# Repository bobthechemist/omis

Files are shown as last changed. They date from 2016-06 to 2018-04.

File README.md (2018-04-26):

## Open Millifluidic Inquiry System ##

The Thingiverse version

The **Open Millifluidic Inquiry System** (OMIS) is a platform for lab-on-a-chip technologies and miniaturized analysis systems. It is a 3D printed, Arduino-based science and engineering project that allows the end-user (student/teacher/hobbyist) to explore the science of fluids. OMIS currently has two parts. The first is a syringe pump constructed from 3D printed parts, an inexpensive stepper motor and some items from the local hardware store. The second part is a “millifluidic device” which is also 3D printed. OMIS is designed with learning and inquiry in mind, and all elements of the design have been created to encourage exploration.

## Quick start
1. Print the parts located in the STL directory.
2. Purchase the items in the [Bill of Materials](documentation/BOM.md).
3. Follow the [build guide](documentation/BuildGuide.md).
4. Design your circuit using [this Adafruit guide](https://learn.adafruit.com/adafruit-arduino-lesson-16-stepper-motors/parts?view=all).
5. Upload the sketch in the software directory to your Arduino.

## Resources
- [The github](http://www.github.com/bobthechemist/omis) repository will be used for version management and issue tracking.  This will be true for design files, software and lessons/activities.
- My [personal webpage](http://www.bobthechemist.com/omis) will be the source for commentary and any opinions I have on the project.
- The build at [Thingiverse](http://www.thingiverse.com/thing:1646999) will remain as the original version for historical reasons.

----------

  
This work is licensed under a <a rel="license" href="http://creativecommons.org/licenses/by-nc-sa/4.0/">Creative Commons Attribution-NonCommercial-ShareAlike 4.0 International License</a>.

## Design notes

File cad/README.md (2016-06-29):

##CAD files

###Syringe pump files
The syringe pump consists of three design files (one for each of the components of the syringe pump), a global variables and functions file and a summary file.  The CAD files have been designed such that the typical changes an end user may make (support rod and lead screw dimensions, fastener types, syringe properties) can all be customized within a single file.

- **sp_global** is the location for all global variables and functions used by the other design files.
- **syringepump** allows the end user to view the entire project.  It is not meant for actual use but to ensure that features and spacing is consistent throughout the design.
- **sp\_motor\_assembly** contains the gear train and components used to hold the stepper motor in place.
- **sp_carriage** is the moving piece that pushes the syringes
- **sp_idler** is the end cap that supports the structural and threaded rods, and also provides support for the syringes.

There are currently two example millifluidic devices, one with side ports and one with top-face ports.  The side-port version uses cylindrical channels and the top-face port version uses rectangular channels.  These devices are designed with exploration in mind, while we identify best practices for 3D printed millifluidic device fabrication.

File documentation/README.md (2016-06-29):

#Table of contents

- have a look at the [Bill of materials](BOM.md) to see what you need to buy.
- Once you have, look at the [Build Guide](BuildGuide.md) for instructions on how to construct the syring pump.

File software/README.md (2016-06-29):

# Arduino sketch and schematic

## Electronics

The breadboard layout, shown below, is identical to the one described in the [Adafruit tutorial on stepper motors](https://learn.adafruit.com/adafruit-arduino-lesson-16-stepper-motors/parts?view=all).  That tutorial is a prerequisite to building the electronics/software side of OMIS.  

breadboard layout

## Sketch

The sketch is broken up into several components, in hopes to make it easier to modify the code.  Note that OMIS uses a modified version of the [Arduino stepper library](https://www.arduino.cc/en/Reference/Stepper).  The primary reason for the modified version is to allow for non-integer RPM values to be passed to the motor.  It also has some helpful(?) functions related to the pump such as determining the volume flow rate for a given motor speed.   Additionally, it contains the operations to be performed when receiving commands via the Serial line.

The other component to the sketch is the Command Parser, which is a very primitive class that deals with serial communication and performs some basic sanity checking.

To install, simply move the software directory and its contents into your Arduino directory, and rename the directory syringepump.

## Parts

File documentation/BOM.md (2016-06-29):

##OMIS Bill of Materials
*Please note this BOM is for the pre-release version (< 1.0) of OMIS and is subject to change*

### General tools and equipment
- 3D printer

    All components of this project were printed on a home-built [Makerfarm](www.makerfarm.com) Prusa 8" i3v.  Presumably, a commercial printer will provide comparable (or more likely, superior) print quality.
- Filament
    
    Builds were tested with PLA (eSun) and PETG (Gizmodorks).  The latter is preferred due to its increased chemical resistance relative to PLA and the structural performance (it is less brittle).

- M3 hex key and wrench
- Exacto knife
- Sandpaper
- Adjustable wrench
- Needle nosed pliers
- Helping hand with magnifier or dissecting microscope 

### syringe pump
- 1/4" steel rod, 140 mm length, (2)
- 1/4"-20 TPI threaded steel rod, 155 mm length (1)
- 5V DC small reduction stepper motor from [Adafruit](https://www.adafruit.com/products/858).
- M3x10 hex-bolts (4)
- M3x16 hex bolts (2)
- M3x25 hex bolts (3)
- M3 hex nuts (12)
- 1/4" 20 TPI nuts (3)
- 1/4" 20 TPI jamnuts (2)
- Syringes

    The default configuration uses a 3-mL HSW luer slip eccentric syringe which can be found at [Restek](http://www.restek.com/catalog/view/8027) although I purchased my batch from Fisher Scientific (and they apprently no longer sell them).  A different syringe can be used by adjusting the parameters in the global file.

### fluidics system
- flexible tubing with an outer diameter of approximately 1.8 mm
- quick-setting epoxy

### controller
- Arduino Uno or similar
- L293D dual H bridge or similar
- hookup wire

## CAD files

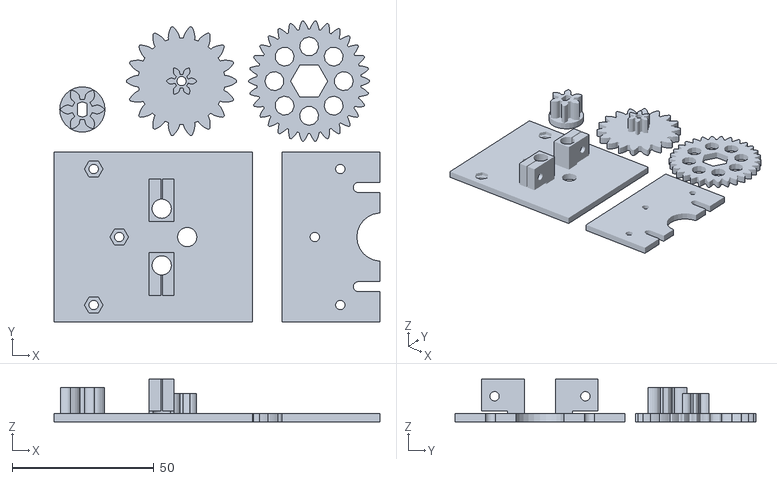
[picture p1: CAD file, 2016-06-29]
stl/motor_assembly.stl
115.0 x 106.2 x 15.0

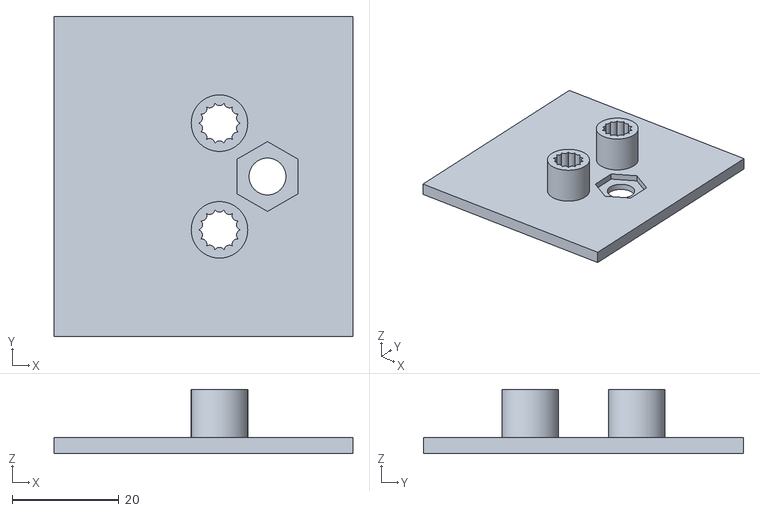
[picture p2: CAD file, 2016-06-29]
stl/carriage.stl
56.0 x 60.0 x 12.0

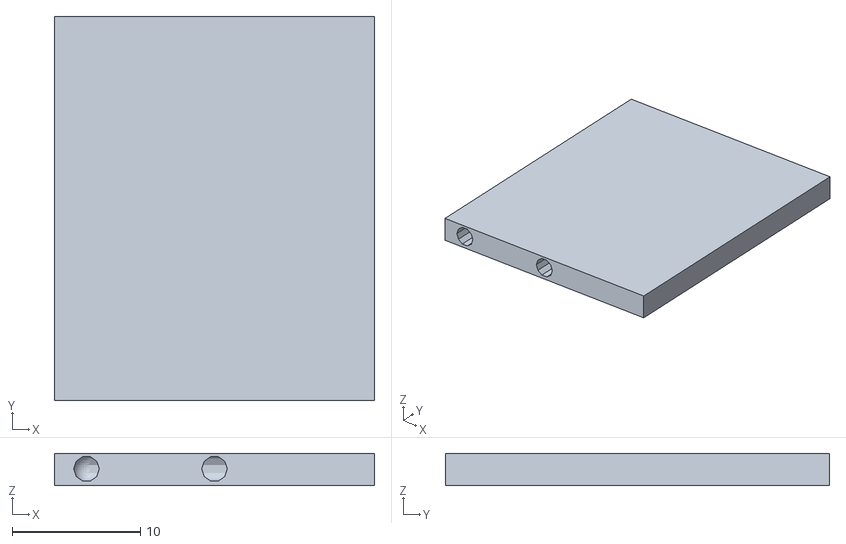
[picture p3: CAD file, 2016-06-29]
stl/cylindricalChannels.stl
25.0 x 30.0 x 2.50

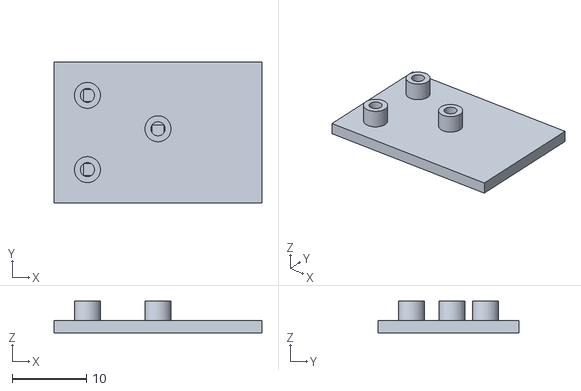
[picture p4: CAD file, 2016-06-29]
stl/rectangularChannels.stl
28.0 x 19.0 x 4.30

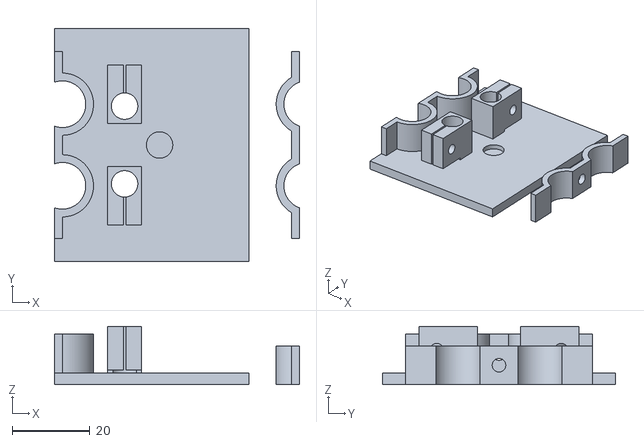
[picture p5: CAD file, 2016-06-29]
stl/idler.stl
63.0 x 60.0 x 15.0

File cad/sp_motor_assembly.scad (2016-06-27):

// Autotitrator motor assembly
/* 
This version incorporates a compound gear train to improve the
torque applied to the lead screw.  Some adjustments made to the
orientation of the suppor rod clamps to allow for printing on one 
side only.

Unlike the first version, this one incorporates gears into the
assembly as opposed to having a separate file.
*/

include <sp_global.scad>;
use <MCAD/involute_gears.scad>;

print_mode = false;

// Gear pitch radii
// 0 is motor, 1 is larger cmpd, 2 is smaller cmpd and 3 is driven
pitchRadius = [5.8333, 17.5, 4, 20];
// Where to put the three support screws, one is aligned with the 
//   compound gear.
gearboxSupport = [ [0,0.4*baseDim[y],0.8*baseDim[z]],
                [0,-0.4*baseDim[y],0.8*baseDim[z]],
                [0,0,
                trodPosition[z]+pitchRadius[2]+pitchRadius[3]]];

// Build up modules
module base(){
    difference(){
        union(){
            translate([0,0,1/2*baseDim[z]])
            cube(baseDim,center=true);
            structuralRodSupports();
        }
        union() {
            threadedRodCutout();
            structuralRodCutout();
            gearboxSupports();
        }
    }
}

module gearboxSupports(){
    // gearbox support holes
    for (i = gearboxSupport) {
        translate(i)
        rotate(90,[0,1,0]){
            cylinder(d=fast[nutDiameter],
                h=1.2*baseDim[y],center=false,$fn=6);
            cylinder(d=fast[boltDiameter],
                h=1.2*baseDim[y],center=true,$fn=25);
        }
    }   
}

module structuralRodSupports() {
    for(i = [ [-1, false], [1, true] ] ){
        translate([baseDim[x]/2, i[0]*rodPosition[y], rodPosition[z]])
        rodClamp(rot=i[1]);
    }    
}

module gearBox(){
    shaft_z = trodPosition[z]+pitchRadius[0] + pitchRadius[1] +
        pitchRadius[2] + pitchRadius[3];
    cmpd_z = trodPosition[z] + pitchRadius[2] + pitchRadius[3];
    difference() {
        union() {
            translate([0,0,1/2*baseDim[z]])
            cube(baseDim,center=true);
            translate([0,0,cmpd_z])
            *rotate(90,[0,1,0]){
                cylinder(d=2.7,h=15,$fn=10);
                cylinder(d=5,h=5);
            }
        }
        union() {
            // motor cutout
            translate([-baseDim[x]/1.9,-baseDim[y]/1.9,baseDim[z]])
            cube([baseDim[x]*1.1,baseDim[y]*1.1,200]);
            translate([0,0,shaft_z])
            rotate(90,[0,1,0])
            cylinder(d=17,h=1.1*baseDim[x],center=true,$fn=25);
            // motor support cutout
            for (i = [-1,1] ) {
                translate([0,i*35/2,shaft_z-8])
                rotate(90,[0,1,0])
                cylinder(d=3.5,h=2.2*baseDim[x],center=true,$fn=25);
                translate([-baseDim[x]/1.9,i*35/2-3.5/2,shaft_z-8])
                cube([baseDim[x]*1.1,3.5,25]);
            }
            // gearbox screw holes
            translate([0,0,cmpd_z])
            rotate(90,[0,1,0])
            cylinder(d=fast[boltDiameter],
                h=1.2*baseDim[y],center=true,$fn=25);
            // gearbox support holes
            for (i = gearboxSupport) {
                translate(i)
                rotate(90,[0,1,0])
                cylinder(d=fast[boltDiameter],
                    h=1.2*baseDim[y],center=true,$fn=25);
            }
            // trim unused part of plate
            translate([0,0,0]);
            cube(1.01*baseDim,center=true);
                
        }
    }
}

module gearDriven(){
    gear_z = 3;
    difference(){
        gear(circular_pitch = 240,
            number_of_teeth = 30, 
            rim_thickness = gear_z,
            hub_thickness = 0,
            gear_thickness = gear_z,
            bore_diameter = 0,
            circles = 8,
            rim_width = 1.5,
            hub_diameter = 15
            );
        cylinder(d=trod[nutDiameter],h=2.1*gear_z,center=true,$fn=6);
    }
}

module gearCompound(){
    gear_z1 = 3;
    gear_z2 = 7;
    difference(){
        union(){
            gear (circular_pitch = 350,
                number_of_teeth = 18,
                rim_thickness = gear_z1,
                hub_thickness = 0,
                gear_thickness = gear_z1,
                bore_diameter = 0
            );
            translate([0,0,gear_z1])
            gear (circular_pitch = 240,
                number_of_teeth = 6,
                rim_thickness = gear_z2,
                hub_thickness = 0,
                gear_thickness = gear_z2,
                bore_diameter = 0,
                rim_width = 0,
                hub_diameter=0
            );
        }
        cylinder(d=fast[boltDiameter]+0.05,
            h=2.1*(gear_z1+gear_z2),center=true,$fn=10);
    }
}

module gearMotor() {
    gear_z = 9;
    difference() {
        translate([0,0,15])
        rotate(180,[0,1,0])
        gear (circular_pitch = 350,
            number_of_teeth=6,
            rim_thickness = gear_z,
            hub_thickness = 12,
            gear_thickness = gear_z,
            bore_diameter = 0,
            hub_diameter=16
        );
        union(){
            translate([0,0,4])
            cylinder(d=5.2,h=3,center=true,$fn=10);
            translate([0,0,0])linear_extrude(16){
                intersection(){
                    circle(d=5.2,$fn=25);
                    square([3.3,5.2],center=true);
                }
            }
        }
    }
}
    
            
    
// Removal modules
module threadedRodCutout(){
    translate([0,trodPosition[y],trodPosition[z]])
    rotate(90,[0,1,0])
    cylinder(d=trod[boltDiameter],
        h=baseDim[x]+2*tol,$fn=25,center=true);
}
module structuralRodCutout(){
    for (i = [-1,1] ) {
        translate([-baseDim[x]/2-tol,
            i*rodPosition[y],rodPosition[z]])
        rotate(90,[0,1,0])
        cylinder(d=srod[boltDiameter],
            h=baseDim[x]+clampDim[x]+2*tol,$fn=25);
    }
}

module motorAssembly(){
    color(color1,1)
    translate([-17.5,0,0])
    gearBox();

    color(color3,0.9)
    translate([-22,0,trodPosition[z]+
        pitchRadius[0]+pitchRadius[1]+pitchRadius[2]+pitchRadius[3]])
    rotate(90,[0,1,0])
    gearMotor();

    color(color4,0.9)
    translate([-12.5,0,trodPosition[z]+pitchRadius[2]+pitchRadius[3]])
    rotate(90,[0,1,0])
    rotate(360/12,[0,0,1])
    gearCompound();
    
    color(color3,0.9)
    translate([-9,trodPosition[y],trodPosition[z]])
    rotate(90,[0,1,0])
    gearDriven();
    
    *translate([-7,0,trodPosition[z]])nut(jam=true);
    *translate([-12.7,0,trodPosition[z]])nut(jam=true);

    color(color1,0.6)
    base();
    

}



whichplate = 0;

if (!print_mode) {
    motorAssembly();
}
else {
    
    // Use an asterick before items you don't want on the build plate.
    translate([-25,0,baseDim[x]/2])
    rotate(90,[0,1,0])gearBox();
    translate([0,0,baseDim[x]/2])
    rotate(90,[0,-1,0])base();
    translate([-60,45,-4.5+baseDim[x]/2])gearMotor();
    translate([20,55,0])gearDriven();
    translate([-25,55,0])gearCompound();
}

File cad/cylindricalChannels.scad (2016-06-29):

//Test leaking with a simple mixer
//Print with 0.2 mm layer height and 0.3 mm first layer

firstlayerheight = 0.2;
layerheight = 0.1;
base = firstlayerheight + layerheight; 
edge = 1.5; // aiming for a 1.5 mm perimeter
cd = 2; //Channel diameter
cr = cd/2; //Channel radius
dx = 20+2*edge+cd;
dy = 30;
dz = base+cd+2*layerheight;

$design = false;

//Rotations to make channel construction easier
y = [-1,0,0];
x = [0,1,0];

module c(h1=1, dir=x) {rotate(90,dir)cylinder(d=cd,h=h1,$fn=10);}
module s() {sphere(d=cd,$fa=5,$fs=0.2);}

module channels() {
    translate([edge+cr,-0.05,base+cr])c(10.05,y);
    translate([edge+cr,10,base+cr])c(20,x);
    translate([edge+cr+20,10,base+cr])c(10,y);
    translate([edge+cr,20,base+cr])c(20,x);
    translate([edge+cr,20,base+cr])c(10.05,y);
    translate([edge+cr+10,-0.05,base+cr])c(10.05,y);
    //joints
    translate([edge+cr,10,base+cr])s();
    translate([edge+cr+20,10,base+cr])s();
    translate([edge+cr+20,20,base+cr])s();
    translate([edge+cr,20,base+cr])s();   
}

module case() {
    cube([dx,dy,dz]);
}



if($design) {
    channels();
    color("blue",0.4)case();
}
else {
    
    difference(){
        case();
        channels();
    }
}

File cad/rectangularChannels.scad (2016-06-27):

/* definitions
v is vertical width (up/down)
h is horizontal width (left/right)
l is length of channel
*/

// When designing, set to true so pieces render in 
//  a cleaner fashion.  **WARNING** objects created
//  with $design = true will not print properly.

$design = true;
$tol = 0.01;


// Channel dimensions, vertical and horizontal widths
cv = 1; ch = 1.6;
// Port dimensions, radius, thickness and height
pr = 0.96; pt = 0.8; ph = 3;
// Device dimensions.  Arbitrary x and y, z determined
//   so there is one base layer and 2 top layers with
//   a 0.2 um layer height and a 0.3 um first layer.
baseDim = [28,19,0.7+cv];

// Device parameters (channels and ports)

// [x,y], horiz width, vert. width, length, direction
channels = [
    [ [0,0], ch, cv, 20, true ],
    [ [0,10], ch, cv, 20, true ],
    [ [20,-ch/2], ch, cv, 10+ch, false ],
    [ [10,0], ch, cv, 6, false ]
];

// [x, y]
ports = [
    [ 0.5, 0 ], 
    [ 10., 5.5 ],
    [ 0.5, 10 ]
];

// Creates a rectangular channel
module ch(h=1,v=0.6,l=10,x=false) {
    
    rotate(x?0:180,[0,0,1])
    rotate(x?90:0,[0,0,1])
    rotate(90,[1,0,0])
    translate([-h/2,0,0])
    linear_extrude(l)square([h,v]);
}



// Takes an array of parameters to create all channels
module makeChannels() {
    for (c=channels) {
        translate([c[0][0],c[0][1],0.3])
        ch(h=c[1],v=c[2],l=c[3],x=c[4]);
    }
}


// Ports are constructed differently for 
module makePortsAdd() {
    for (p=ports) {
        translate([p[0],p[1],cv+.3])
        cylinder(r=pr+pt,h=ph,$fn=100);
    }
}
module makePortsSubtract() {
    for (p=ports) {
        translate([p[0],p[1],0.3+cv-($design?$tol:0)])
        cylinder(r=pr,h=($design?2*$tol:0)+ph,$fn=100);
    }
}
module makePorts() {
    difference() { 
        makePortsAdd(); 
        makePortsSubtract();
    }
}

module makeCase() {
    translate([-4,-4.5,0])
    cube(baseDim);
}

if($design) {
    makeChannels();
    makePorts();
    color("blue",0.4)makeCase();
}
else {
    difference() {
        union(){
            makeCase();
            makePortsAdd();
        }
        union() {
            makeChannels();
            makePortsSubtract();
        }
    }
}

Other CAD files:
cad/sp_carriage.scad
cad/sp_global.scad
cad/sp_idler-old.scad
cad/sp_idler.scad
cad/syringepump.scad

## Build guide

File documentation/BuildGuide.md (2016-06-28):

#Syringe pump build guide

##Step 1. Gather your parts
Print the three parts to the syringe pump (idler, carriage, and motor assembly).  Make sure you have collected all the necessary items from the bill of materials.  Additionally, some tools (needle nose pliers, adjustable wrench, and M3 wrenches) will be helpful.

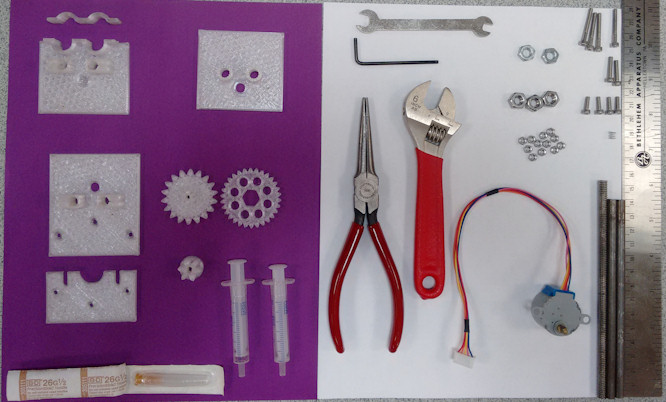
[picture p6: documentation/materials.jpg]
materials


##Step 2. Idler assembly
- We'll start with the hardest part first (unless you have very tiny fingers).  Place an M3 nut in each of the support rod nut traps of the idler.  Sometimes, getting the nut almost positioned and then squeezing it down with the needle nose pliers is helpful; just be careful not to snap off the support rod clamp. 
- The syringe support is connected with a M3x24 bolt.  The spring is optional but I find it helpful when loading/unloading the syringes as it keeps tension on the nut and prevents it from turning.  My 'source' of the spring was an empty retractable ball point pen; I happened to find one with the right diameter (a bit larger than the M3 bolt diameter) and cut it to size.

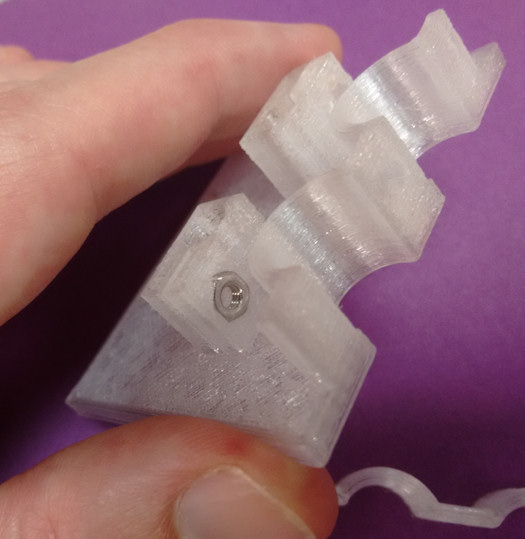
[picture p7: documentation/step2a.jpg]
The idler nut traps are the trickest place to reach


*The idler nut traps are the trickest place to reach*  

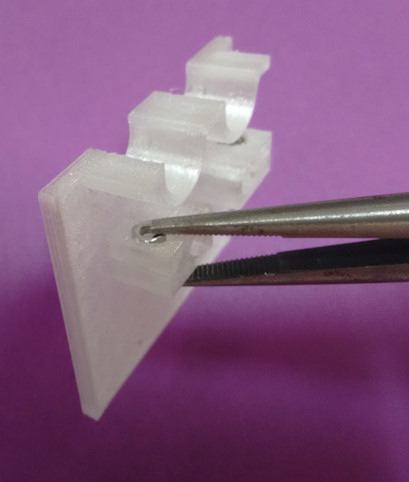
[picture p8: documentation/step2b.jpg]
use needle nose pliers to help
 

 *use needle nose pliers to help*  

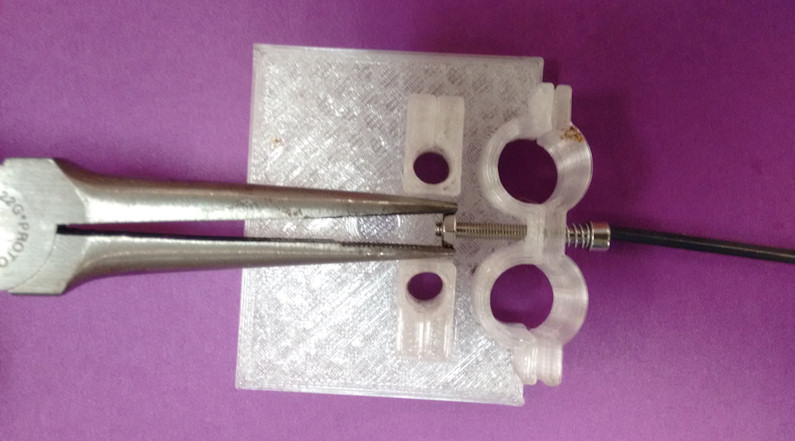
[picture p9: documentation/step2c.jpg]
An optional spring makes inserting/removing the syringes easier
  

 *An optional spring makes inserting/removing the syringes easier*   

##Step 3. Support rods
- Slide the support rods into their clamps and push them through until the ends are flush with the idler.  Use M3x10 bolts to clamp the rods tightly.  If you cannot rotate the rods easily, then you have tightened sufficiently.

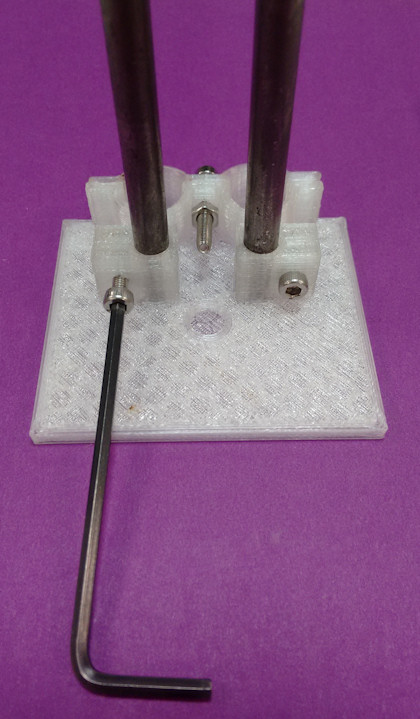
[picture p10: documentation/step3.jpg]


*Some cracking sound while tightening is OK; that's the support material.  Don't overdo it though.*

##Step 4. Threaded rod and carriage
- Slide the carriage on to the support rods with the linear bearings facing away from the idler.  Insert the threaded rod (also known as a lead screw) through the carriage and into its slot in the idler.  
- Thread one nut for the carriage, then an additional nut and a jamnut (the nut that is thinner) onto the lead screw.  None of the nuts need to be tight at this point and all of them should be lower than the height of the support rods.

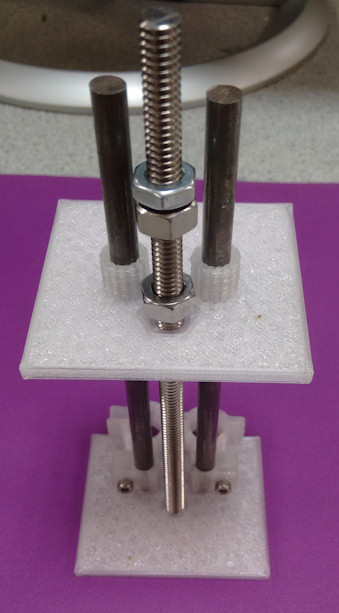
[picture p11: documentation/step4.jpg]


*Hmm, [what is a jam nut](https://en.wikipedia.org/wiki/Jam_nut)?*

##Step 5. Motor Assembly support plate
- Similar to step 3, connect the support rods to the motor assembly support plate.  Tighten the support clamps after you are sure that the syringe pump stands level and the carriage moves smoothly across the support rods.
- If the support rod clamps are sufficiently tightened, then you should not be able to twist the pump while holding the idler in one hand and the motor assembly support plate in the other.

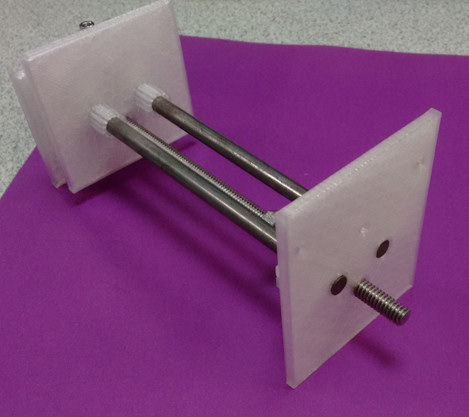
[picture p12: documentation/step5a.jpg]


*The support rods should not extend beyond the motor support plate or they will hit one of the gears.*

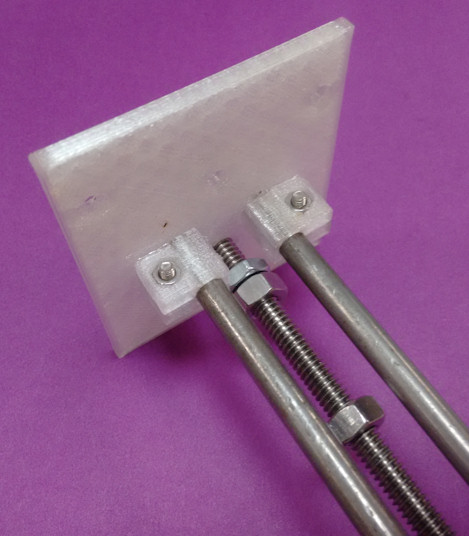
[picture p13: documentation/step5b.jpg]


*Make sure the syringe pump sits level on the table before tightening the support rod clamps.*

##Step 6. Adjust jam nut stop
- We now learn what the jam nut is for.  It will prevent the lead screw from "unscrewing" out of our syringe pump.
- Thread the jam nut so that it touches the motor assembly support plate.  Then, turn it about 1/2 turn the opposite direction so it is not tightly against the plate.
- Thread the regular nut so that it contacts the jam nut, taking care not to turn the jam nut and lose the space between it and the plate that you just created.
- Hold the jam nut with the needle nosed pliers and with the adjustable wrench, tighten the nut so that it is "jammed" up against the jam nut.  When you have done this correctly, neither the jam nut nor the normal nut will move on the lead screw

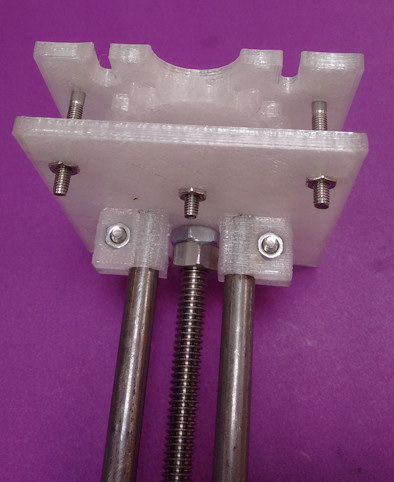
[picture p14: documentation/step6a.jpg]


*You want the jam nut as close to the motor assembly support plate as possible without rubbing against it causing unnecessary friction.*

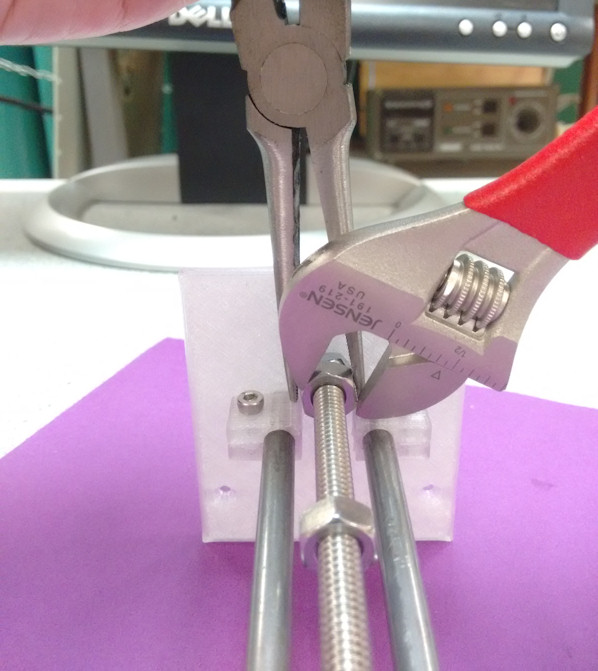
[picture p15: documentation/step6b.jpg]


*In the direction of this picture, turn the wrench clockwise and apply a counter-clockwise pressure to the pliers.*

##Step back, admire your work
By "admire" I mean this is a good time to go over the build to ensure that everything is working properly.  The lead screw should turn freely in both directions and it should not come out of the idler support hole.  The support rods should be firmly in place and the pump should stand level on a flat surface.  You should be able to slide the free nut on the lead screw into the nut trap on the carriage.  Then turning the lead screw should move the carriage back and forth. 

##Step 7. Install the driven gear
- Press a regular sized nut into the driven gear.  The gear is thinner than the nut and that is OK.
- Thread a jam nut onto the lead screw just as you did in step 6.  Thread the driven gear onto the lead screw, making sure that the side of the gear that is flush with the nut is pointing away from the motor assembly plate.
- As in step 6, secure the nut holding the driven gear to the jam nut, leaving very little space between the plate and the jam nut.

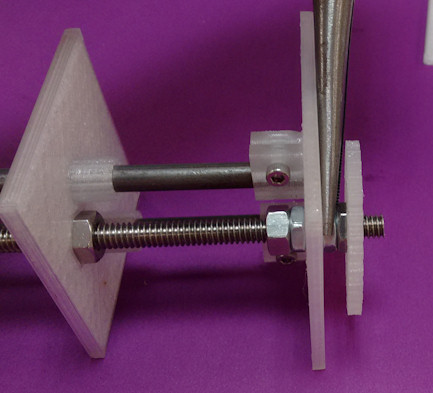
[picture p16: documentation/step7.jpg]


*Use the same procedure as in step 6, but note that you can tighten by twisting the gear instead of using a wrench.*

##Step 8. Install remaining motor assembly
- Install M3 nuts into the nut traps on the motor assembly support plate.  
- Slide the compound gear onto one of the M3x24 bolts.  Make sure that the gear rotates freely on the axis.  It is possible that you may need to strip away a small bit of plastic from the compound gear bore.  This can be done by inserting a screw into the bore part way, then hammering the screw through.  Do this from both sides of the compound gear. 
- Use  3 M3x24 bolts (including the one with the compound gear on it) to attach the back plate to the motor assembly.  Be careful not to over-tighten these screws.  The compound gear should sit between the driven gear and the backplate and should be perpendicular to the table.

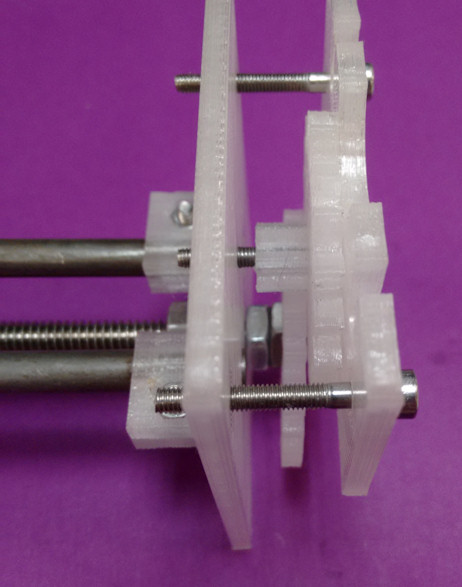
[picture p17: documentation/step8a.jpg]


*Better to have the M3x24 bolts too loose than too tight.  You can always tighten them if the gears slip.*

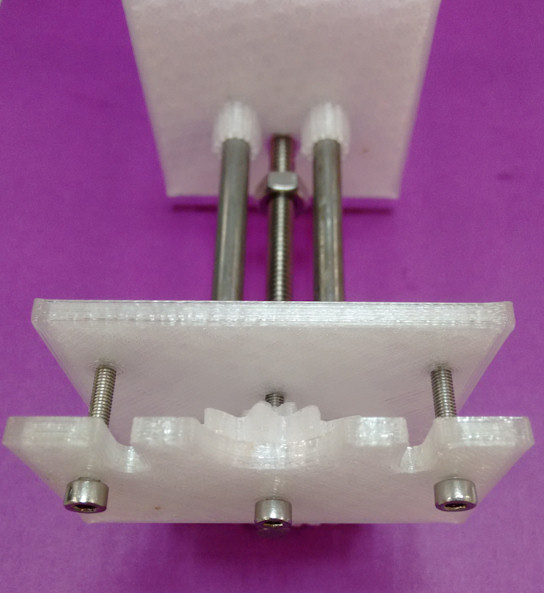
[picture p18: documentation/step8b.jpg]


*Try spinning the gears to ensure smooth operation.  Once the motor is attached, the gears won't spin as easily.*

##Step 9. Attach motor gear
- Attach the motor gear to the stepper motor.  It is possible that this is a very tight fit.  You can use a sharp blade to cut away some of the plastic if necessary.
- Attach M3x20 bolts with four nuts as shown in the picture.  Nothing should be tightened at this point.

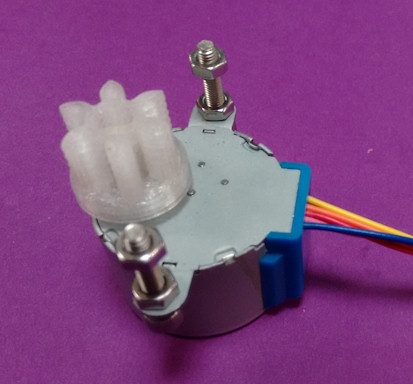
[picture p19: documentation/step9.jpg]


*Note that the motor gear bore is slotted so that it will only attach to the motor one way.*

##Step 10. Mount the motor.
- The back plate should slide in between the two nuts.  Use these to secure the motor in place.  Proper alignment of the motor is with the bolts settled into the bottom of the cutout.
 
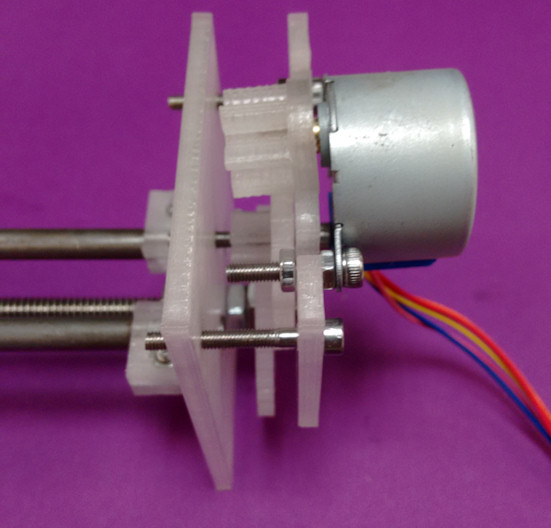
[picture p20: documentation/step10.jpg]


*Using an M3 wrench on the M3 nut will help secure everything in place*

##Build complete
You now have a completed syringe pump and are ready to go on to the next step - setting up the control hardware and communication software.

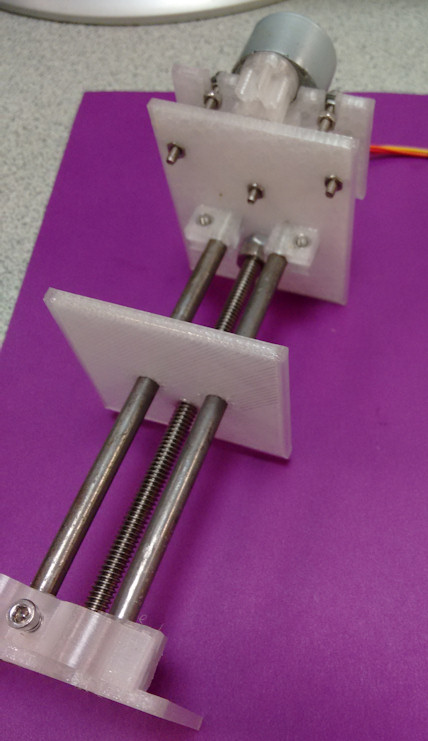
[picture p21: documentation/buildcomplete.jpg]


*Nice job!*

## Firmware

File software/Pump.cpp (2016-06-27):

/*
 * Pump.cpp - Stepper library for syringe pump, based off:
 * Stepper.cpp - Stepper library for Wiring/Arduino - Version 1.1.0
 * 
 * Modifications:
 * - step_delay is now type float allowing for more precise speed selections
 * - setSpeed accepts type float per above
 * - added pump data to constructors (mechanicalAdvantage, threadsPerMillimeter, syringLinearVolumeRatio)
 * - added syringe math (e.g. calculate number of steps needed to deliver a given volume.)
 * - added command structure
 * - changed `step` to accept long type
 */

#include "Arduino.h"
#include "Pump.h"

/*
 * two-wire constructor.
 * Sets which wires should control the motor.
 */
Pump::Pump(int number_of_steps, int motor_pin_1, int motor_pin_2,
            float mechanicalAdvantage, float threadsPerMillimeter, 
            float syringeLinearVolumeRatio)
{
  this->step_number = 0;    // which step the motor is on
  this->direction = 0;      // motor direction
  this->last_step_time = 0; // time stamp in us of the last step taken
  this->number_of_steps = number_of_steps; // total number of steps for this motor

  // Arduino pins for the motor control connection:
  this->motor_pin_1 = motor_pin_1;
  this->motor_pin_2 = motor_pin_2;

  // setup the pins on the microcontroller:
  pinMode(this->motor_pin_1, OUTPUT);
  pinMode(this->motor_pin_2, OUTPUT);

  // When there are only 2 pins, set the others to 0:
  this->motor_pin_3 = 0;
  this->motor_pin_4 = 0;
  this->motor_pin_5 = 0;

  // pin_count is used by the stepMotor() method:
  this->pin_count = 2;

  // setup pump data
  this->mechanicalAdvantage = mechanicalAdvantage;
  this->threadsPerMillimeter = threadsPerMillimeter;
  this->syringeLinearVolumeRatio = syringeLinearVolumeRatio;
}


/*
 *   constructor for four-pin version
 *   Sets which wires should control the motor.
 */
Pump::Pump(int number_of_steps, int motor_pin_1, int motor_pin_2,
            int motor_pin_3, int motor_pin_4, float mechanicalAdvantage, 
            float threadsPerMillimeter, float syringeLinearVolumeRatio)
{
  this->step_number = 0;    // which step the motor is on
  this->direction = 0;      // motor direction
  this->last_step_time = 0; // time stamp in us of the last step taken
  this->number_of_steps = number_of_steps; // total number of steps for this motor

  // Arduino pins for the motor control connection:
  this->motor_pin_1 = motor_pin_1;
  this->motor_pin_2 = motor_pin_2;
  this->motor_pin_3 = motor_pin_3;
  this->motor_pin_4 = motor_pin_4;

  // setup the pins on the microcontroller:
  pinMode(this->motor_pin_1, OUTPUT);
  pinMode(this->motor_pin_2, OUTPUT);
  pinMode(this->motor_pin_3, OUTPUT);
  pinMode(this->motor_pin_4, OUTPUT);

  // When there are 4 pins, set the others to 0:
  this->motor_pin_5 = 0;

  // pin_count is used by the stepMotor() method:
  this->pin_count = 4;

  // setup pump data
  this->mechanicalAdvantage = mechanicalAdvantage;
  this->threadsPerMillimeter = threadsPerMillimeter;
  this->syringeLinearVolumeRatio = syringeLinearVolumeRatio;
}

/*
 *   constructor for five phase motor with five wires
 *   Sets which wires should control the motor.
 */
Pump::Pump(int number_of_steps, int motor_pin_1, int motor_pin_2,
            int motor_pin_3, int motor_pin_4, int motor_pin_5,
            float mechanicalAdvantage, float threadsPerMillimeter, 
            float syringeLinearVolumeRatio)
{
  this->step_number = 0;    // which step the motor is on
  this->direction = 0;      // motor direction
  this->last_step_time = 0; // time stamp in us of the last step taken
  this->number_of_steps = number_of_steps; // total number of steps for this motor

  // Arduino pins for the motor control connection:
  this->motor_pin_1 = motor_pin_1;
  this->motor_pin_2 = motor_pin_2;
  this->motor_pin_3 = motor_pin_3;
  this->motor_pin_4 = motor_pin_4;
  this->motor_pin_5 = motor_pin_5;

  // setup the pins on the microcontroller:
  pinMode(this->motor_pin_1, OUTPUT);
  pinMode(this->motor_pin_2, OUTPUT);
  pinMode(this->motor_pin_3, OUTPUT);
  pinMode(this->motor_pin_4, OUTPUT);
  pinMode(this->motor_pin_5, OUTPUT);

  // pin_count is used by the stepMotor() method:
  this->pin_count = 5;

  // setup pump data
  this->mechanicalAdvantage = mechanicalAdvantage;
  this->threadsPerMillimeter = threadsPerMillimeter;
  this->syringeLinearVolumeRatio = syringeLinearVolumeRatio;  
}

/*
 * Sets the speed in revs per minute
 */
void Pump::setSpeed(float whatSpeed)
{
  this->step_delay = 60.0 * 1000.0 * 1000.0 / 
    this->number_of_steps / constrain(whatSpeed,this->minRPM,this->maxRPM);
}

/*
 * Moves the motor a number of revolutions
 * Simply wraps `step` with the total number of steps
 */
void Pump::turn(float revolutions) {
  this->step(int(revolutions * this->number_of_steps));
}

/*
 * Moves the motor steps_to_move steps.  If the number is negative,
 * the motor moves in the reverse direction.
 */
void Pump::step(long steps_to_move)
{
  long steps_left = abs(steps_to_move);  // how many steps to take

  // determine direction based on whether steps_to_mode is + or -:
  if (steps_to_move > 0) { this->direction = 1; }
  if (steps_to_move < 0) { this->direction = 0; }


  // decrement the number of steps, moving one step each time:
  while (steps_left > 0)
  {
    unsigned long now = micros();
    // move only if the appropriate delay has passed:
    if (now - this->last_step_time >= this->step_delay)
    {
      // get the timeStamp of when you stepped:
      this->last_step_time = now;
      // increment or decrement the step number,
      // depending on direction:
      if (this->direction == 1)
      {
        this->step_number++;
        if (this->step_number == this->number_of_steps) {
          this->step_number = 0;
        }
      }
      else
      {
        if (this->step_number == 0) {
          this->step_number = this->number_of_steps;
        }
        this->step_number--;
      }
      // decrement the steps left:
      steps_left--;
      // step the motor to step number 0, 1, ..., {3 or 10}
      if (this->pin_count == 5)
        stepMotor(this->step_number % 10);
      else
        stepMotor(this->step_number % 4);
    }
  }
}

/*
 * Moves the motor forward or backwards.
 */
void Pump::stepMotor(int thisStep)
{
  if (this->pin_count == 2) {
    switch (thisStep) {
      case 0:  // 01
        digitalWrite(motor_pin_1, LOW);
        digitalWrite(motor_pin_2, HIGH);
      break;
      case 1:  // 11
        digitalWrite(motor_pin_1, HIGH);
        digitalWrite(motor_pin_2, HIGH);
      break;
      case 2:  // 10
        digitalWrite(motor_pin_1, HIGH);
        digitalWrite(motor_pin_2, LOW);
      break;
      case 3:  // 00
        digitalWrite(motor_pin_1, LOW);
        digitalWrite(motor_pin_2, LOW);
      break;
    }
  }
  if (this->pin_count == 4) {
    switch (thisStep) {
      case 0:  // 1010
        digitalWrite(motor_pin_1, HIGH);
        digitalWrite(motor_pin_2, LOW);
        digitalWrite(motor_pin_3, HIGH);
        digitalWrite(motor_pin_4, LOW);
      break;
      case 1:  // 0110
        digitalWrite(motor_pin_1, LOW);
        digitalWrite(motor_pin_2, HIGH);
        digitalWrite(motor_pin_3, HIGH);
        digitalWrite(motor_pin_4, LOW);
      break;
      case 2:  //0101
        digitalWrite(motor_pin_1, LOW);
        digitalWrite(motor_pin_2, HIGH);
        digitalWrite(motor_pin_3, LOW);
        digitalWrite(motor_pin_4, HIGH);
      break;
      case 3:  //1001
        digitalWrite(motor_pin_1, HIGH);
        digitalWrite(motor_pin_2, LOW);
        digitalWrite(motor_pin_3, LOW);
        digitalWrite(motor_pin_4, HIGH);
      break;
    }
  }

  if (this->pin_count == 5) {
    switch (thisStep) {
      case 0:  // 01101
        digitalWrite(motor_pin_1, LOW);
        digitalWrite(motor_pin_2, HIGH);
        digitalWrite(motor_pin_3, HIGH);
        digitalWrite(motor_pin_4, LOW);
        digitalWrite(motor_pin_5, HIGH);
        break;
      case 1:  // 01001
        digitalWrite(motor_pin_1, LOW);
        digitalWrite(motor_pin_2, HIGH);
        digitalWrite(motor_pin_3, LOW);
        digitalWrite(motor_pin_4, LOW);
        digitalWrite(motor_pin_5, HIGH);
        break;
      case 2:  // 01011
        digitalWrite(motor_pin_1, LOW);
        digitalWrite(motor_pin_2, HIGH);
        digitalWrite(motor_pin_3, LOW);
        digitalWrite(motor_pin_4, HIGH);
        digitalWrite(motor_pin_5, HIGH);
        break;
      case 3:  // 01010
        digitalWrite(motor_pin_1, LOW);
        digitalWrite(motor_pin_2, HIGH);
        digitalWrite(motor_pin_3, LOW);
        digitalWrite(motor_pin_4, HIGH);
        digitalWrite(motor_pin_5, LOW);
        break;
      case 4:  // 11010
        digitalWrite(motor_pin_1, HIGH);
        digitalWrite(motor_pin_2, HIGH);
        digitalWrite(motor_pin_3, LOW);
        digitalWrite(motor_pin_4, HIGH);
        digitalWrite(motor_pin_5, LOW);
        break;
      case 5:  // 10010
        digitalWrite(motor_pin_1, HIGH);
        digitalWrite(motor_pin_2, LOW);
        digitalWrite(motor_pin_3, LOW);
        digitalWrite(motor_pin_4, HIGH);
        digitalWrite(motor_pin_5, LOW);
        break;
      case 6:  // 10110
        digitalWrite(motor_pin_1, HIGH);
        digitalWrite(motor_pin_2, LOW);
        digitalWrite(motor_pin_3, HIGH);
        digitalWrite(motor_pin_4, HIGH);
        digitalWrite(motor_pin_5, LOW);
        break;
      case 7:  // 10100
        digitalWrite(motor_pin_1, HIGH);
        digitalWrite(motor_pin_2, LOW);
        digitalWrite(motor_pin_3, HIGH);
        digitalWrite(motor_pin_4, LOW);
        digitalWrite(motor_pin_5, LOW);
        break;
      case 8:  // 10101
        digitalWrite(motor_pin_1, HIGH);
        digitalWrite(motor_pin_2, LOW);
        digitalWrite(motor_pin_3, HIGH);
        digitalWrite(motor_pin_4, LOW);
        digitalWrite(motor_pin_5, HIGH);
        break;
      case 9:  // 00101
        digitalWrite(motor_pin_1, LOW);
        digitalWrite(motor_pin_2, LOW);
        digitalWrite(motor_pin_3, HIGH);
        digitalWrite(motor_pin_4, LOW);
        digitalWrite(motor_pin_5, HIGH);
        break;
    }
  }
}

/*
  version() returns the version of the library:
*/
int Pump::version(void)
{
  return 1;
}

// Debugging
float Pump::debug(void)
{
  return this->step_delay;
}

// find RPM for a given flow rate;
float Pump::FRtoRPM(float flowRate)
{
  return flowRate * this->syringeLinearVolumeRatio / 1000.0 * 
    this->threadsPerMillimeter * this->mechanicalAdvantage;
}

// find flow rate fora given RPM
float Pump::RPMtoFR(float rpm)
{
  return rpm / this->mechanicalAdvantage / this->threadsPerMillimeter * 
    1000.0 / this->syringeLinearVolumeRatio;
}

// find # steps to deliver desired volume (in uL)
float Pump::VOLtoSTEPS(float volume)
{
  return volume / 1000.0 * this-> syringeLinearVolumeRatio * this->threadsPerMillimeter * 
    this->mechanicalAdvantage * this->number_of_steps;
}

// find # steps to move plunger <distance> millimeters 
float Pump::DISTtoSTEPS(float distance) 
{
  return distance * this->threadsPerMillimeter * this->mechanicalAdvantage * this->number_of_steps;
}

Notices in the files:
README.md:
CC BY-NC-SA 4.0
